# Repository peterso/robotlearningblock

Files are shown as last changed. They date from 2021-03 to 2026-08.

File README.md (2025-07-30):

# robotlearningblock

Welcome to the project repository for the Internet-connected task board, an electronic real-world benchmarking platform for evaluating robot manipulation skills. This project, known as the Digital Robotic Judge, or DR.J, contains the complete design of competition task boards used in the [Robothon Grand Challenge](https://www.robothon-grand-challenge.com) and the [euROBIN Manipulation Skill Versatility Challenge](http://sites.google.com/view/eurobin-msvc/home) to remotely assess manipulation performances over the Internet. Trial attempts are recorded by an on-board microcontroller which verifies the execution time and successful task completion through performance circuits. Task board telemetry is automatically published on a [web dashboard](https://cloud.kaaiot.com/wd-public/c1v9jqmgul2l1s47m6bg/dashboards/0d2f0e4c-6a80-4cf4-a48d-5b25fcb35ac0/50cdf30f-955e-4ccf-b13a-8e1d0281f68a?public_id=4e4990d1-dcab-4f1a-b1a6-8648e87bc5ad). The best automated robot solutions are collected, ranked, and verified with an expert jury over a video conference call. The top copmetition results are posted on a [leaderboard](http://github.com/peterso/robothon-grand-challenge) and developers are encouraged to share their project code in the form of competition submissions so that others can reproduce and improve on their results.

Industrial use cases collected through a survey are incorporated into the design of portable electronic task boards and made available to the community of robot developers to solve and put forth their best automated solution. New task board designs are developed annually. Share your use case to be considered in upcoming designs with the [Use Case Survey Google Form](https://forms.gle/XueGB4yPwioggSN97).

If you find this work helpful, please cite our [IEEE-RAM paper](https://ieeexplore.ieee.org/document/10378967). 

The concept of a crowdsourced robot solution for real-world use cases with the DR.J pipeline is shown below.

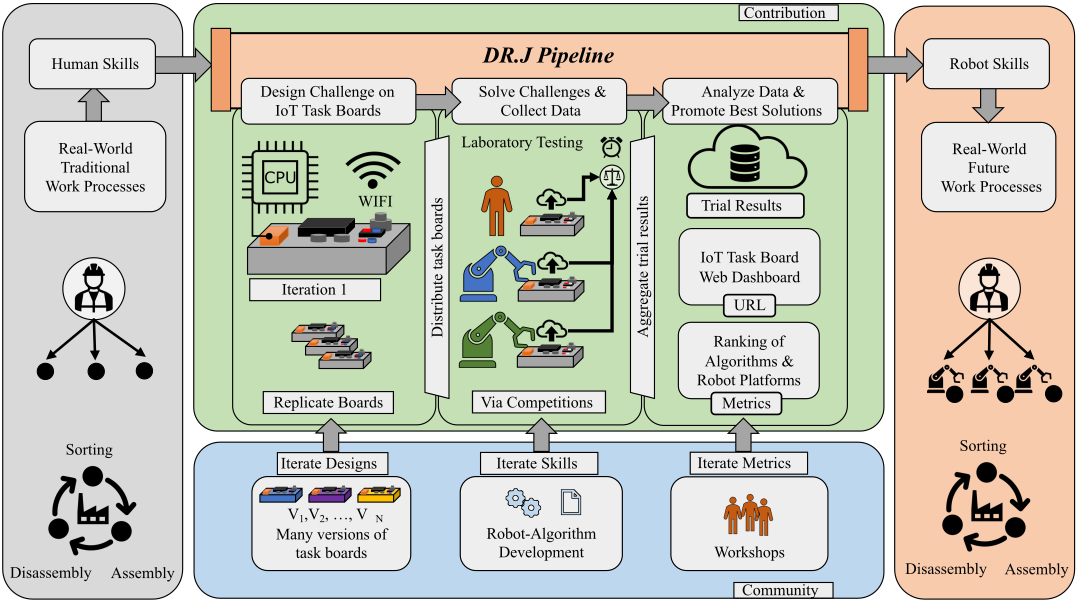
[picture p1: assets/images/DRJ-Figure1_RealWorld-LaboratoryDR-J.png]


## Quick Links

- IEEE-RAM Paper Digital Robot Judge: [DOI: 10.1109/MRA.2023.3336473](https://doi.org/10.1109/MRA.2023.3336473)
- 1-min Paper [Highlight Video](https://drive.google.com/file/d/1jVCkPBq7-JO2KUGaQfxDcgK1_qGyWVMT/view) 
- ERF 2022 Hackathon: Franka Emika Tactile Manipulation Benchmark Challenge: [Highlight Video](https://www.youtube.com/watch?app=desktop&v=eqpV09Kuc_o)
- Robothon Grand Challenge Competition [automatica website](https://automatica-munich.com/en/munich-i/robothon/)
- IROS 2024 Competiton: [euROBIN Manipulation Skill Versatility Challenge](http://sites.google.com/view/eurobin-msvc/home)
- Links to Web Dashboards for Deployed Task Boards:
  - [TBv2023: Teams Single Board View](https://cloud.kaaiot.com/wd-public/c1v9jqmgul2l1s47m6bg/dashboards/0d2f0e4c-6a80-4cf4-a48d-5b25fcb35ac0/50cdf30f-955e-4ccf-b13a-8e1d0281f68a?public_id=4e4990d1-dcab-4f1a-b1a6-8648e87bc5ad)
  - [TBv2023: Subtask Completion Times](https://cloud.kaaiot.com/wd-public/c1v9jqmgul2l1s47m6bg/dashboards/a8b5be5f-cc23-4724-8f06-3f67f8fef104?public_id=4e4990d1-dcab-4f1a-b1a6-8648e87bc5ad)
  - [TBv2021: Teams Single Board View](https://cloud.kaaiot.com/wd-public/c1v9jqmgul2l1s47m6bg/dashboards/dashboard2/931cb10a-3044-49c8-8530-5ce0951e291b?public_id=4e4990d1-dcab-4f1a-b1a6-8648e87bc5ad)
- Task Board Telmetry Emulator in Python (browser-based) [Replit](https://replit.com/@peterso/TaskBoardSimulator?v=1)
- Simulated Task Board Model on Mujoco for Offline Skill Development [Multiverse Github Project](https://github.com/Multiverse-Framework/Multiverse-Objects/tree/main/task_board)
- Request a physical task board [Task Board Request Google Form](https://forms.gle/EJiNF4A1qsrMpy8i6)
- Propose new tasks for future board designs [Use Case Survey Google Form](https://forms.gle/XueGB4yPwioggSN97)

## Project Description

The goal of the project is to provide an objective tool for measuring manipulation performance for both humans and robots. A microcontroller on the task box monitors the state of the mounted manipulation elements and reports state change events to a cloud-hosted dashboard to aggregate performance data. Device telemetry, including accelerometer data, is regularly logged to provide insight into the device's usage. Manipulation tasks are designed with objects that can be electronically verified to be in their designated start and goal positions. Trial protocols define sequences of actions on the task board and allow designers to create test scenarios. The execution time of subtasks within a protocol are recorded and automatically published on a web dashboard for consistent and convenient comparison with previous trial attempts. A modular framework for adding new task board objects was selected to encourage community members to design and build their own trial protocols.

An example demonstration of the internet-connected task board can be viewed on [YouTube](https://www.youtube.com/watch?v=1jdvIbDURSA). Here is the very first test run with a Franka Emika Panda robot in the lab [YouTube](https://youtu.be/LJFTypNZrFs).

A screenshot of a web dashboard from the 2021 Robothon Grand Challenge competition.

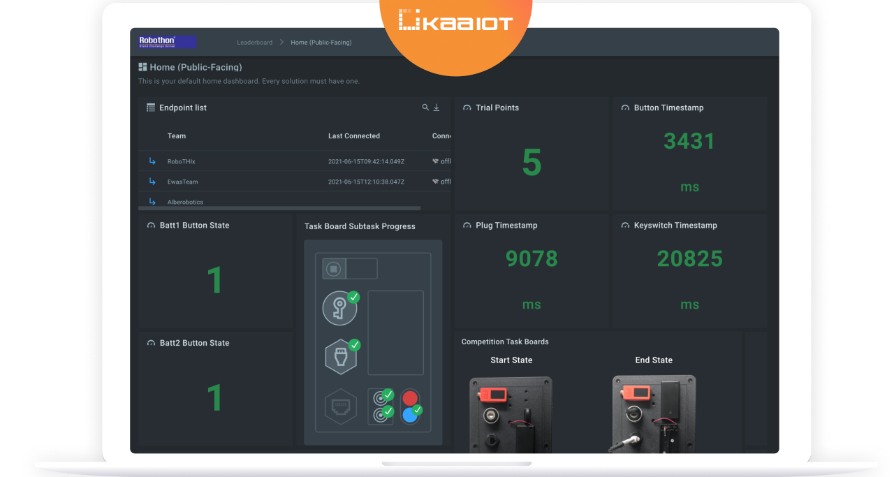
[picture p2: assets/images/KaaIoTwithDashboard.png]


Just for fun: The name is borrowed from the legendary basketball star [Julius "DR.J" Irving](https://www.youtube.com/watch?v=bWLXcg-V8FI). 

#### A little history on the smart task board development...
The internet-connected task board was first featured during the internationl robot manipulation competition, [Robothon Grand Challenge](https://www.robothon-grand-challenge.com) at automatica in 2021. The design of the task board has been expanded and reimplemented for the competition again in 2022 and has also been picked up by the pan-European robotics excellence collaboration project, [euROBIN](https://www.eurobin-project.eu/).

Here is an example setup of a exemplary robot testing setup with the task board.

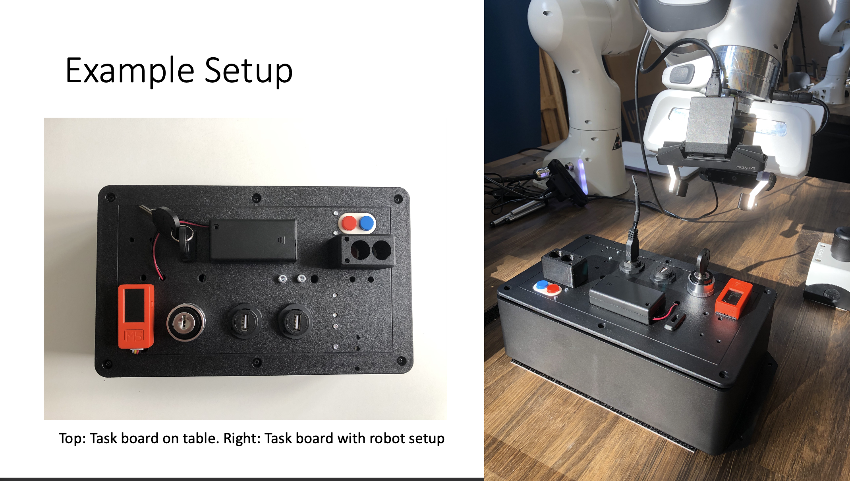
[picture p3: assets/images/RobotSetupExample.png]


The electronic task board allows for the direct comparison between a human and a robot performance to quantitatively measure the gap.

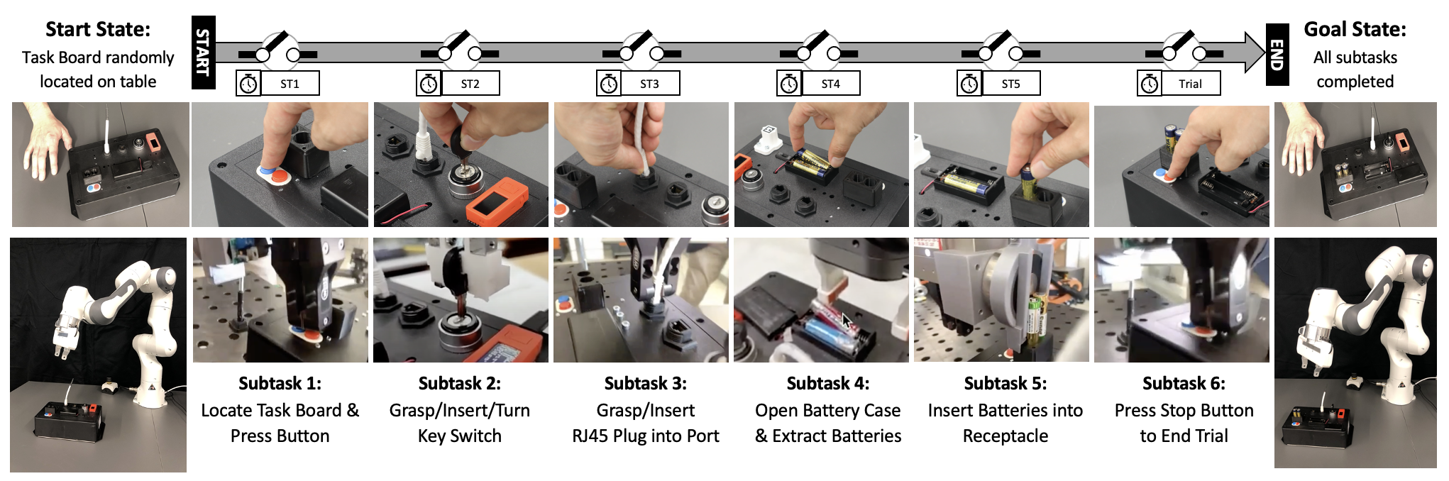
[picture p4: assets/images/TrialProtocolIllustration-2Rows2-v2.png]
TrialProtocolHumanRobot


Here is the trial protocol for the task board version TBv2021 used in the Robothon Grand Challenge in 2021 and 2022 to guide roboticists to develop reusable manipulation skills for e-waste sorting and disassembly.

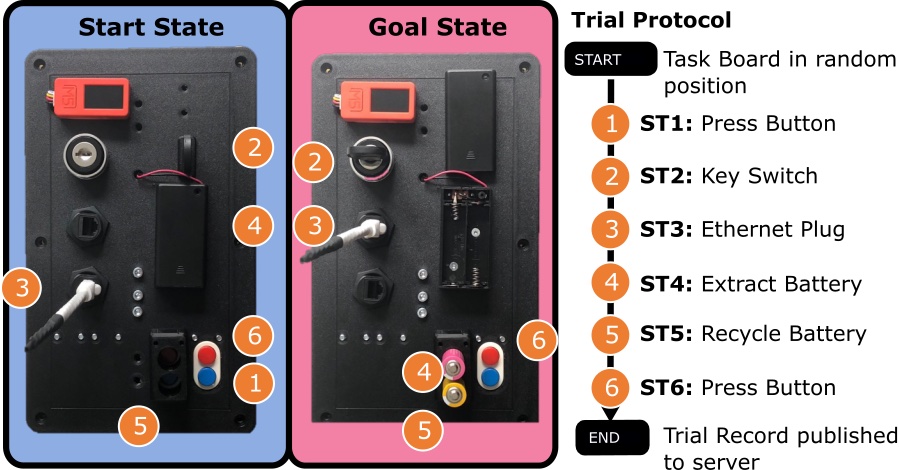
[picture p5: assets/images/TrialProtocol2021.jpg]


A new task board design (TBv2023) was designed and built to develop manipulation skills in performing electronic device assessments with a multimeter. The design was also adapted to meed the needs of the euROBIN network and was used in the Robothon Grand Challenge in 2023.

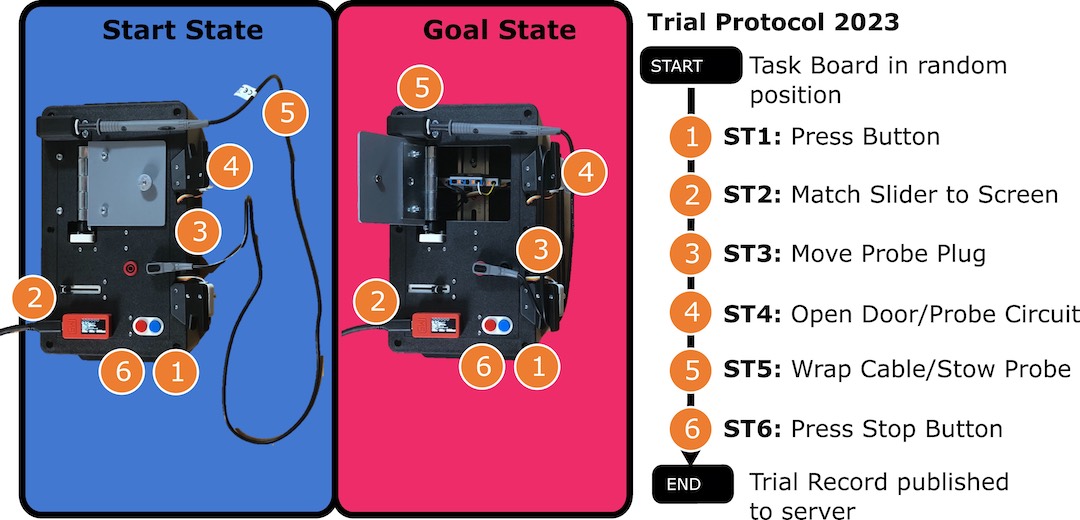
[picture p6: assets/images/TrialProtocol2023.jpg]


As part of the competition, teams were challenged to demonstrate the manipulation skills of their robot platform on an e-waste object of their choice in the "Bring-Your-Own-Device (BYOD) Challenge". Below are some examples of the successful demonstrations. 

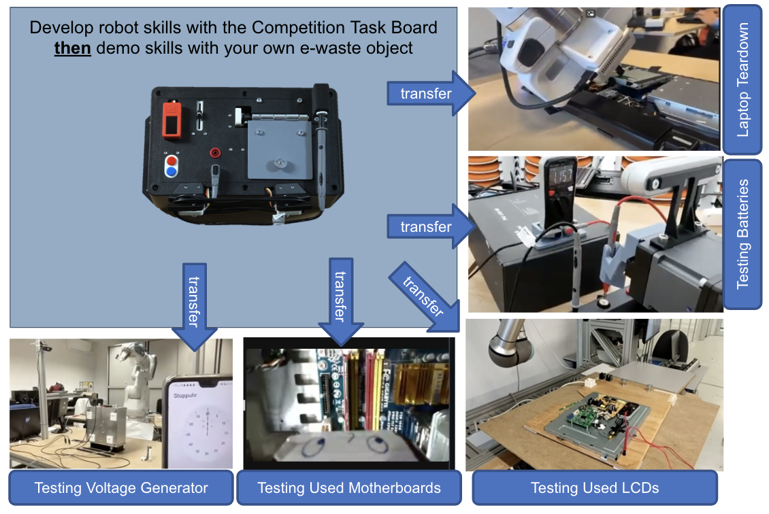
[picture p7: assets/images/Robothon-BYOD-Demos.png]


### Quick Start to connect a Task Board to the Web Dashboard

The microcontroller (orange component) has 3 Buttons and a USB-C charge/programming port:
- ***Power Button*** (side closest to USB-C), 
- ***Button A*** (next to screen, labeled M5), 
- ***Button B*** (side furthest from USB-C).

#### Turning on the Task Board ####

1. Toggle Power Manually = Hold Power Button for 2 seconds to turn on and 6 seconds to turn off.
2. Plugging in the uController will automatically turn on the device.

#### Connect board to the web dashboard over the internet with your preferred WiFi Network using your laptop or smartphone

1. Connect to Task Board SSID: “AutoConnectAP-task-board-###” where ### refers to the number on the sticker on the side of the box (Password: “robothon”)
2. A configuration screen should automatically open in a browser on your device. Otherwise, open web browser and go to URL: “192.168.4.1”.

3. Click the ”Configure” button to setup a new WiFi network connection. 

4. Select Desired WiFi from the scanned list.

5. Enter your SSID's WiFi password.

6. Click the “Save” Button. The new credentials will be saved to the microcontrollers EEPROM memory for future connections. The Task Board will attempt to connect to new WiFi. After it has successfully connected to the Internet over the new network the Home Screen will be displayed on the screen. 

#### Begin running experiments with the task board

1. Ensure the task board components are on their starting position prior to starting. The uController will display an alert on the screen if it detects an incorrect starting configuration.
2. Press Button A to start recording a trial run! Trial runs will be automatically recorded to the web dashboard. Scan the QR code on the sticker for more information.
3. Reset Trial Clock after a trialèPress Button B to reset the clock to zero.

#### Some Other Helpful Tips:

  • ***Offline/Local Mode:*** Use your task board without the internet by holding Button A down when powering on the device.

  • ***Abort an Active Trial:*** Stop an ongoing trial early by holding down the Red Push Button and pressing Button A.

### Detailed User Instructions 

The task board is designed to capture manipulation performance for use in the [Robothon Grand Challenge](https://www.robothon-grand-challenge.com). The microcontroller tracks users overall trial completion time, intermediate subtask completion times, earned trial points, and cumulative interaction force. Performance trials are initiated by the user after restoring the components to their start configuration and then pressing the M5 button. A countdown timer ends trial attempts after 10 minutes. When the task board is connected to the internet, the microcontroller publishes telemetry, during an active trial at 20Hz and 0.2Hz when idle, to a remote cloud server. An interactive web dashboard renders the trial data from the task board to provide transparent, remote observability into performance trials. Trials end when the countdown timer expires or when all sub-tasks are completed and the user presses the red stop button. Final trial results are displayed on the task board LED display and on the web dashbaord.

Trial protocols have a programmed time out of 10 minutes. While a trial is active, a red LED is illuminated on the controller. During active trials the agent under test should follow the trial protocol and complete all 5 subtasks on the task board as fast as possible. The results are recorded locally on the device and displayed on the controller's LED screen. 

Link to a [web simulator](https://replit.com/@peterso/TaskBoardSimulator?v=1) with Replit for testing new task board designs and trial protocols. NOTE: you will need to generate a new device token on the KaaIoT platform. 

Prior to running a new trial attempt, the trial protocol specifies the user must pick up and randomly place the task board in a new location in front of the user. An example of the location initialization is shown in the .gif below.

InitializeTaskBoard

After the task board location has been initialized, the user then presses the Trial Start button (M5 button) to begin a logged trial attempt. This .gif shows a human actor solving the 2021 trial protocol.

ManualTrialRun

#### Reading Task Board State over USB

When working with the task board, developers may want to read the task board state directly from the task board controller instead of referring to the web dashboard. To do this, use the python utility file to record the output to a local CSV file. See `/python/scripts/read-serial.py`.

### Core Design Features

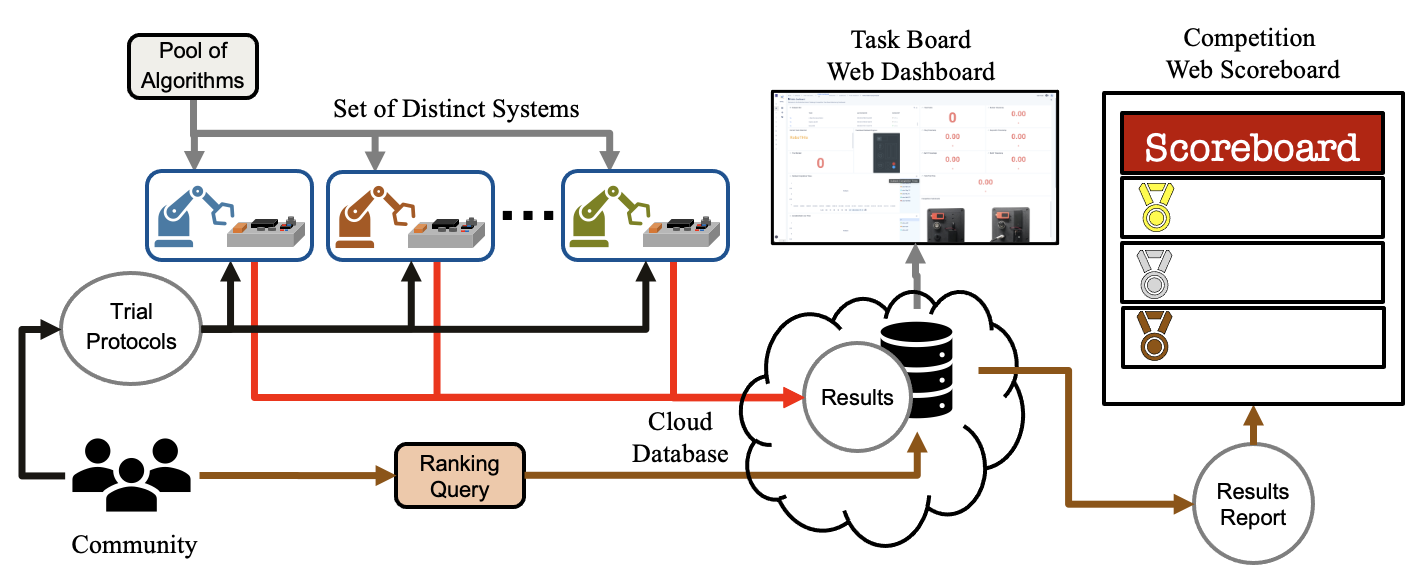
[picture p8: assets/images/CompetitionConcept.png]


The core design features of the task board microcontroller are:

**[Status] Feature Description**

- [x] task board monitors a digital state of all mounted manipulation elements
- [x] user can start a trial using the device without internet connection
- [x] task board reports the timestamps for each successful task interaction trial over USB
- [x] report the state of the task box over WiFi to the [Kaa internet dashboard](https://www.linkedin.com/safety/go?url=https%3A%2F%2Fcloud.kaaiot.com%2Fwd-public%2Fc1v9jqmgul2l1s47m6bg%2Fdashboards%2F0d2f0e4c-6a80-4cf4-a48d-5b25fcb35ac0%2F19addcfa-9cf1-42b3-8bd3-32a1feb4abdb%3Fpublic_id%3D4e4990d1-dcab-4f1a-b1a6-8648e87bc5ad&trk=flagship-messaging-web&messageThreadUrn=urn%3Ali%3AmessagingThread%3A2-YWRhYjQ3ZGYtZjc2YS00ZjZmLTkyZWEtMmMxNGNlNWE0ZjVjXzAxMw%3D%3D&lipi=urn%3Ali%3Apage%3Ad_flagship3_feed%3BBN9Td%2Bo8RjSi2fSXdyBvfQ%3D%3D) 
- [x] setup wifi greeter to allow user to supply own wifi ssid and password
- [x] report the state of the task box over USB
- [x] task board reports are integrated into a Microsoft Azure IoT dashboard
- [x] device has a digital twin that can be represented in a robot simulator i.e. Gazebo, Mujoco. 
- [ ] report the load cell readings on the task box surface
- [ ] integrate bluetooth power meter into task board telemetry
- [ ] enable internet connection network support for "Eduroam"

### NEW Feature Requests

- [x] Over-The-Air Updates to deploy new trial protocols to task boards in the field
- [x] Make the task board surface more stiff/rigid -> removed load cell and mount top plate to housing directly
- [ ] Add a automated testing procedure for a contract manufacturer to execute prior to shipping task boards
- [ ] Look into Device Management with BalenaOS for multiple OTA updates as an alternative to Kaa OTA
- [ ] Add ROS messages to the task board microcontroller to broadcast task results to robots

Please make a Github pull request with an updated README to add your new feature requests. Task board designs are updated annually and the firmware is continuously improved based on user feedback.

### Design Goals & System Architecture

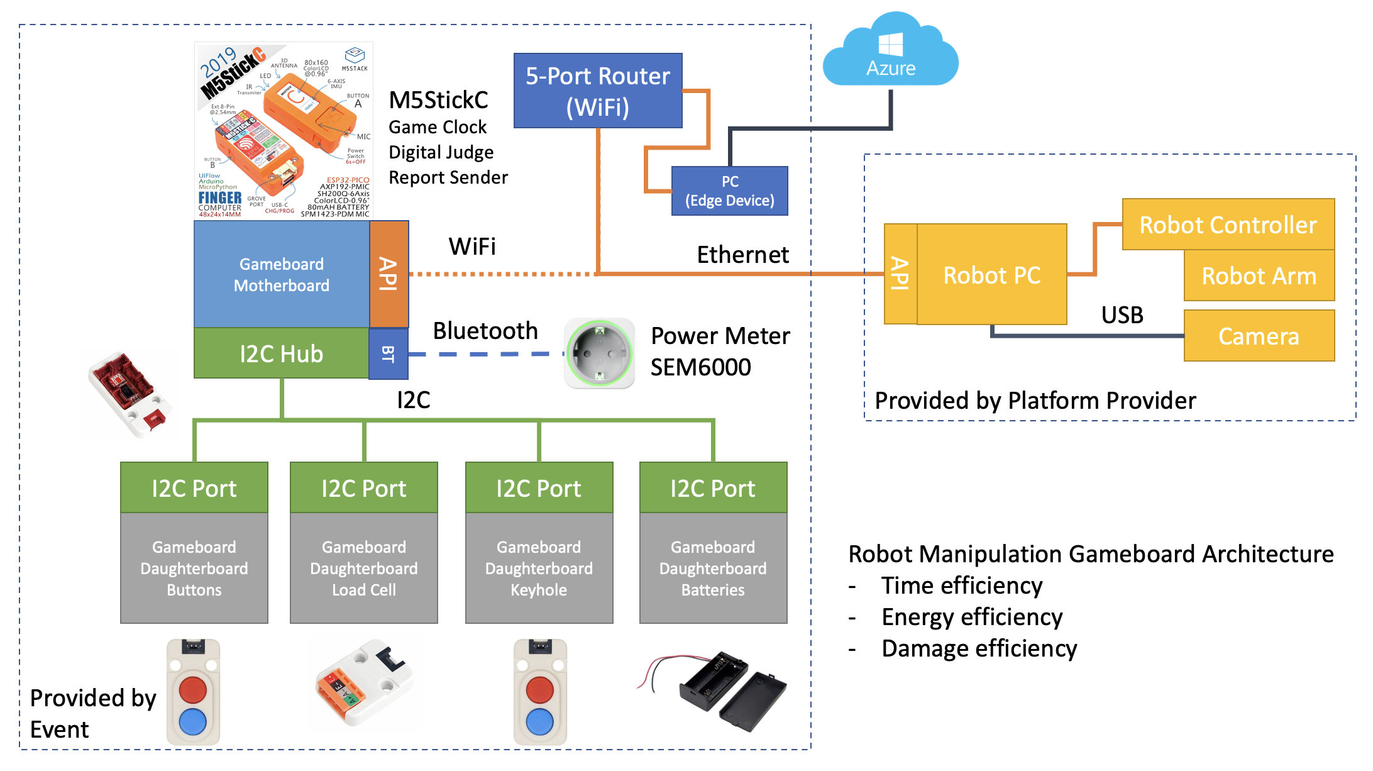
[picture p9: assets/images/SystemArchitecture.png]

Each task board is equipped with a microcontroller to remotely monitor its state and track usage statistics. Task boards are designed with the following features in mind:
- ***Affordable.*** Task board components should not exceed $200 to allow community members to build their own. The design is intended to be open sourced and remixed. 
- ***Portable.*** Task boards will have the capability to record trials untethered on battery power.
- ***Shippable.*** Task boards should be about the size of a laptop and weigh less than 1kg. For competition events, task boards can be shipped to participants to ensure everyone receives the same physical demonstrator setup.
- ***Traceability.*** Experiments performed on the task board can be automatically logged to a central web server for community members to share their development journey as well as easily download their experimental results.
- ***Extensible.*** Task board IO is extendable over an I2C bus to incorporate new task elements in future designs. 
- ***Networked.*** Each task board has the ability to report recorded trials to an online database.

### Relevant Design Documents

| Design Document       | TBv2021 | TBv2023 | TBv2025 |
|-----------------------|---------|---------|--------|
| Design BOM            | [TBv2021](https://docs.google.com/spreadsheets/d/1id1LLbRTHQwQDf9HCM8Hft5gwp9QI8y8CJt2JUEMMQk/edit?usp=sharing)        | [TBv2023](https://drive.google.com/file/d/1Rnd_u9MT5yowWGOLc9BP8yHH_inwEdMb/view?usp=sharing)        | Coming Soon |
| Assembly Drawing      | [PDF](https://drive.google.com/file/d/1hJSEHZe9U0Q7VRQKNKOsz96tIN9Y0mhF/view?usp=sharing)        | [PDF](https://drive.google.com/file/d/1tS-sQoqfd0bgX27vQssPpRKi-OBj2Tsp/view?usp=sharing)        |  Coming Soon |
| CAD Files             | [Onshape](https://cad.onshape.com/documents/9a15cff68aad2604a1373593/w/144a51d8ddacf96586ad0e0d/e/052e579b24ce3c66ae263023)        | [Onshape](https://cad.onshape.com/documents/db5a4ee49311d077447cc358/w/9c0b93db9a3945ee3cde6ada/e/5ab54cca5c27c6df318a9a63?renderMode=0&uiState=6720a79a1d02e666789b5f03)        |  [Onshape](https://cad.onshape.com/documents/aecd2bd76f7413bc4958e89c/w/35208a35a382e053eafac0d7/e/f99d3f5cc522bc6d6c1e4afb) |
| Assembly Instructions | [PDF](https://drive.google.com/file/d/1Znj0Do6tISIWl07lZ31Lp-qGyfQIPycp/view?usp=sharing)        | [PDF](https://drive.google.com/file/d/1LZS_wPafdJOO1Q0lu-8TDO9xGrxpoSBB/view?usp=sharing)        |  Coming Soon |
| Wiring Diagram | [PNG](/assets/images/TaskBoard-5Level-Wiring.png)        | [PDF](https://drive.google.com/file/d/1LZS_wPafdJOO1Q0lu-8TDO9xGrxpoSBB/view?usp=sharing)        |  Coming Soon |
| 3D Print Files        | ./assets        | ./assets        |  Coming Soon |
| CNC Files             | ./assets        | ./assets        |  Coming Soon |

### Task Board Deployment History
- ***2021*** An initial 15 task boards were fabricated for the Robothon 2021 competition at automatica.
- ***2022*** 20 task boards were built for the Robothon 2022 competition.
- ***2023*** A new design was released for Robothon 2023. 20 task boards were made for the competition.
- ***2024*** 15 more task boards (TBv2023) were made for the [euROBIN project](https://www.eurobin-project.eu/).
- ***2025*** A new design was released for Robothon 2025. 10 task boards were produced and distributed. 
- ***Order your own task board*** If you are interested in getting a pre-assembled task board to demonstrate your robot platform's capabilities or to follow along in the robot benchmark, please write an e-mail request with the model year [TBv2021/TBv2023/TBv2025] and the number of boards you wish to have along with your mailing address to peter@modularmotions.com.

### Circular Economy Articles inspiring Manipulation Task Selection
- WEF Report on battery recycling [Link to Article](https://www3.weforum.org/docs/WEF_A_New_Circular_Vision_for_Electronics.pdf)
- German Battery Collection with GRS Batterien [Link to Article](https://www.en.grs-batterien.de/grs-batterien/)
- Fun video from Curiousity Quest showing many e-waste handling processes [YouTube Video](https://www.youtube.com/watch?v=lMn-sDvgj4Q&ab_channel=curiosityquest)

### References
- [M5Stack Docs](https://docs.m5stack.com/)
- [M5Stack Community Forum](https://community.m5stack.com/category/17/m5-stick-stickc)
- [KaaIoT Arduino SDK](https://github.com/kaaproject/kaa-arduino-sdk)
- European Robotics Forum 2022 Franka Emika Tactile Manipulation Benchmark Challenge [Highlight Video](https://www.youtube.com/watch?app=desktop&v=eqpV09Kuc_o)
- 2022 Robothon Grand Challenge at [automatica/munich_i](https://www.robothon-grand-challenge.com), [Digital Kickoff Meeting Slides](https://drive.google.com/file/d/1OdqM9bOmNVIISuL4vuRz019WOS697p_8/view?usp=sharing), Award Ceremony [YouTube](https://www.youtube.com/watch?v=im-amiwJDgc&t=1s)
- 2023 Robothon Grand Challenge at [automatica/munich_i](https://www.robothon-grand-challenge.com), [Digital Kickoff Meeting Slides](https://drive.google.com/file/d/1x1t6U09iTEmM228orjCqwZNxu3CphAaz/view?usp=share_link), Award Ceremony [YouTube](https://www.youtube.com/watch?v=YmOT24pqiHU&t=559s)
- euROBIN Manipulation Skill Versatility Challenge at IROS 2024 [Competition Website](http://sites.google.com/view/eurobin-msvc/home)
- 2025 Robothon Grand Challege at [automatica/munich_i](https://automatica-munich.com/en/munich-i/robothon/)

### Citation 
If you find this work insightful to your research or you reference data from our competitions, please cite this work as ***Digital Robot Judge (DR.J): Building a Task-Centric Performance Database of Real-World Manipulation with Electronic Task Boards***. The manuscript is accepted for publication in IEEE Robotics and Automation Magazine as an open-access publication and an early release is available on [IEEE-Xplore](https://ieeexplore.ieee.org/document/10378967).

Bibtex:
```
@ARTICLE{So2024DRJ,
  author={So, Peter and Sarabakha, Andriy and Wu, Fan and Culha, Utku and Abu-Dakka, Fares J. and Haddadin, Sami},
  journal={IEEE Robotics & Automation Magazine}, 
  title={Digital Robot Judge: Building a Task-centric Performance Database of Real-World Manipulation With Electronic Task Boards}, 
  year={2023},
  volume={},
  number={},
  pages={2-14},
  doi={10.1109/MRA.2023.3336473}}
```

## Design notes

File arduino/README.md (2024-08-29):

# README Arduino Setup

The project is developed with the Arduino IDE.

If you want to flash the firware onto the M5StickPlus (ESP32) device then you will need to download the Arduino IDE and make the following changes to your configuration.

## Setup the Arduino IDE for the M5StickC

1. Add the M5Stack Library to your Library Path in Preferences [Github](https://docs.m5stack.com/en/quick_start/m5stickc_plus/arduino)
2. Install the "ESP32 Arduino" and "M5StickCPlus" Library using the Board Library Manager
3. Install the Wifi Manager Greeter "tzapu" using the Library Manager [Github](https://github.com/tzapu/WiFiManager#install-through-library-manager)

## How to flash new firmware onto your task board with Arduino IDE

1. Plug in the task board M5StickPlus unit to your PC with a USB cable.
2. Select the new device under the Port menu.
3. Select the board type as "M5StickC" under the Tools/Board menu.
4. Open the project folder containing the file you want to flash and compile and upload the .ino file. You should see an upload complete message in the command output section.
5. Verify the new firmware is working as expected by examining the serial output using the Serial Monitor tool.

## How to flash new firmware without the Arduino IDE
Use the flash-bin-no-ide.zip folder as a shareable object with the client. Compile the new target firmware with the Arduino IDE and then copy the *.bin files from your local PC into a new .zip folder.

The location of the *.bin files after compiling will be listed in the Arduino IDE in the terminal output when "verbose" flag for compiling is on in the Preferences menu. On a Mac, the location is something like: `/var/folders/bf/p280vkg91qj8wl5_1w4gn32h0000gn/T/arduino_build_168910/`

For Linux

Run the following two commands in a shell. Note, the second command parameters may need to be adapted depending on the file name during the binary export process and the port the task board controller is bound to.

`$ cd <PATH-to-UNZIPPED-FILES>`

`$ python esptool.py --chip esp32 --port /dev/ttyUSB0 --baud 1500000 --before default_reset --after hard_reset write_flash -z --flash_mode dio --flash_freq 80m --flash_size detect 0xe000 ./boot_app0.bin 0x1000 ./bootloader_dio_80m.bin 0x10000 ./stopwatch_m5stickcplus.ino.bin 0x8000 ./stopwatch_m5stickcplus.ino.partitions.bin`

Tip: On Linux, if you get a permission denied error on /dev/ttyUSB0 try the following command:
`sudo chmod a+rw /dev/ttyUSB0`

## Helpful Coding Resources
- M5Stack LCD Library Documentation: https://github.com/m5stack/m5-docs/blob/master/docs/en/api/lcd.md 
- ESP32 Persistent Memory Example: https://randomnerdtutorials.com/esp32-save-data-permanently-preferences/

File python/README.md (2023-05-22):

# README

### Setup PC to read the task board state over USB:
1. Install dependencies
`python -m pip install pyserial`

2. Grant access rights to the USB Port (Linux)
`sudo chmod 666 /dev/ttyUSB0`

3. Plug in the M5Stick Controller to the PC with a USB cable and verify the device is connected
`lsusb`

4. Open a new terminal window and run the python script `read-serial.py`

### Quick Start
A python script for reading input from a USB serial port and saving the streamed data to a file.

Run python script.
`python scripts/read-serial.py`

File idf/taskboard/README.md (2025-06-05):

# Robothon Task Board Firmware

A flexible and extensible firmware for Robothon Task Board.

Noteworthy features:

- Configurable task execution system with configurable patterns
- Modular sensor monitoring framework based on M5Stack
- REST API and Web Interface for remote control
- ROS 2 integration with custom message types
- Leaderboard logging and performance tracking

## Table of Contents

- [Robothon Task Board Firmware](#robothon-task-board-firmware)
  - [Table of Contents](#table-of-contents)
  - [Build firmware](#build-firmware)
  - [Data Model Overview](#data-model-overview)
    - [SensorMeasurement](#sensormeasurement)
    - [Sensor](#sensor)
    - [TaskStep](#taskstep)
    - [Task](#task)
  - [Controller Architecture Overview](#controller-architecture-overview)
    - [TaskBoardDriver](#taskboarddriver)
      - [Default Task](#default-task)
    - [ScreenController](#screencontroller)
    - [TaskExecutor](#taskexecutor)
    - [NonVolatileStorage](#nonvolatilestorage)
    - [HTTPServer](#httpserver)
    - [JSONHandler](#jsonhandler)
    - [WifiManager](#wifimanager)
    - [micro-ROS controllers](#micro-ros-controllers)
  - [Accessing the data model](#accessing-the-data-model)
    - [Example applications](#example-applications)
      - [REST API](#rest-api)
      - [Getting status from ROS 2](#getting-status-from-ros-2)
      - [Triggering a new Task from ROS 2](#triggering-a-new-task-from-ros-2)
      - [Triggering Task Board default task from ROS 2](#triggering-task-board-default-task-from-ros-2)
  - [Common actions](#common-actions)
    - [Connecting to a Wi-Fi network](#connecting-to-a-wi-fi-network)
    - [Connecting to a micro-ROS Agent](#connecting-to-a-micro-ros-agent)
      - [Using Docker](#using-docker)
      - [Building the micro-ROS Agent](#building-the-micro-ros-agent)
      - [Configuring the micro-ROS Agent](#configuring-the-micro-ros-agent)
    - [Recording a ROS 2 session](#recording-a-ros-2-session)
  - [Over-The-Air (OTA) updates](#over-the-air-ota-updates)
  - [Developing the Web Interface](#developing-the-web-interface)

## Build firmware

> [!IMPORTANT]
Make sure to configure the specific controller hardware and partition filename needed for your board as explained below in the menuconfig step.

The Robothon Task Board Firmware is built on top of the ESP-IDF framework.

The easiest way to get started is to use the ESP-IDF Docker image:

```bash
# Enter ESP-IDF Docker image
docker run -it --rm -v /dev:/dev --privileged espressif/idf:release-v5.3

# Install dependencies inside the Docker container
pip3 install catkin_pkg lark-parser colcon-common-extensions empy==3.3.4

# Clone the repository
git clone https://github.com/peterso/robotlearningblock

# Initialize the submodules
cd robotlearningblock
git submodule update --init --recursive

# Change to the project directory
cd /robotlearningblock/idf/taskboard

# Configure the project
idf.py menuconfig
# M5STACK controller -> M5STACK hardware (Select the hardware of the M5 HW on your board)
# Partition Table -> Custom partition CSV file
#     "partitions.csv" (default) for M5STACK StickC Plus2 and M5STACK CORE2
#     "partitions_stickcplus.csv" for M5STACK StickC Plus (version with 4MB of FLASH memory)

# Deploy to the board and monitor execution
idf.py build flash monitor
```

To update a `M5STACK StickC Plus` (the version with 4MB of FLASH memory), it is necessary to use a different baud rate for flashing:

```bash
# Deploy to the board and monitor execution
idf.py build && idf.py -b 500000 flash && idf.py monitor
```

To run `idf.py` from any additional terminal attached to the Docker, the following command is needed:

```bash
source /opt/esp/idf/export.sh
```

## Build ROS 2 messages

In case that the ROS 2 messages are modified, they need to be built from a ROS 2 environment.

This is only necessary when the compiler shows an error similar to this:

```bash
/robotlearningblock/idf/taskboard/main/microros/MicroROSTypes.hpp:217:27: error: 'robothon_taskboard_msgs__msg__TaskStatus' {aka 'struct robothon_taskboard_msgs__msg__TaskStatus'} has no member named 'score'
```

To build the ROS 2 messages run `colcon build` in the `extra_ros_packages` directory.

```bash
# Navigate to the messages directory
cd extra_ros_packages

# Build the messages
colcon build

# Source the ROS 2 workspace
source install/local_setup.bash
```

If the above commands are not available in your current environment, it is possible to start a ROS 2 Jazzy Docker container to read and modify the files in the host filesystem via a shared volume.

```bash
# Go to the taskboard directory in your host filesystem
cd robotlearningblock/idf/taskboard

# Run the Jazzy Docker container with a volume pointing to the current directory
docker run -it --rm --privileged --net=host -v $(pwd):/robotlearningblock/idf/taskboard ros:jazzy

# Navigate to the messages directory
cd /robotlearningblock/idf/taskboard/extra_ros_packages

# Build the messages
colcon build

# Source the ROS 2 workspace
source install/local_setup.bash
```

After building the messages, go back to the espressif environment, clean the project and build it again:

```bash
# Clean and build the project
idf.py clean
idf.py build
```

If you used the ROS 2 Jazzy Docker approach, to point to the already existing project in your host filesystem, you can also use the Docker volume option with the ESP-IDF container:

```bash
# Go to the repository root
cd robotlearningblock

# Run the ESP-IDF Docker container with a volume pointing to the current directory
docker run -it --rm -v /dev:/dev -v $(pwd):/robotlearningblock --privileged espressif/idf:release-v5.3

# Navigate to the taskboard directory inside the Docker container
cd /robotlearningblock/idf/taskboard

# Clean and build the project
idf.py clean
idf.py build
```

## Data Model Overview

The Robothon Task Board Firmware is built around a hierarchical data model where **Tasks** is the main component.

A **Task** is a named group of **TaskSteps** that must be completed in an specific order.

A **TaskStep** is a single condition that must be met during task execution.
It is composed of a **Sensor** and a **SensorMeasurement**.

It is fulfilled when the **Sensor** reading matches the expected value defined in the **SensorMeasurement**.

A **Sensor** represents a physical or aggregated input device that can be read, updated, and monitored.

An example of a physcal **Sensor** can be a button attached to a GPIO.
On the other hand an aggregated **Sensor** can be a virtual sensor that combines multiple physical sensors, for example the activation of two buttons at the same time.

A **SensorMeasurement** represents a single reading from a sensor.

This element holds a value and a type.
Types can be boolean values, analog values or even complex values like a 3D vector.

```mermaid
classDiagram
    class Task
    class TaskStep
    class Sensor
    class SensorMeasurement

    Task "1" *-- "1..*" TaskStep : contains
    TaskStep *-- Sensor : monitors
    TaskStep *-- SensorMeasurement : expects
    Sensor --> SensorMeasurement : produces
```

### SensorMeasurement

**SensorMeasurement** are represented globally in `SensorMeasurement` class found in `sensor/SensorMeasurement.hpp`.

Current implementation has support for:

| Type      | Description   | C++ Type                     |
| --------- | ------------- | ---------------------------- |
| `BOOLEAN` | Boolean value | `bool`                       |
| `ANALOG`  | Analog value  | `float`                      |
| `VECTOR3` | 3D vector     | `SensorMeasurement::Vector3` |

### Sensor

**Sensor** are represented globally in `Sensor` class found in `sensor/Sensor.hpp`.

Beyond that, there is also provided a `AnalogFilteredSensor` class in`sensor/AnalogFilteredSensor.hpp` that extends `Sensor` and adds a averaging filter to the analog readings.

### TaskStep

**TaskStep** are represented globally in `TaskStep` class found in `task/TaskStep.hpp`.

Currently, there are three types of `TaskStep`:

- `TaskStepEqual`: Exact value matching with configurable tolerance.
- `TaskStepGreaterEqualThan`: Threshold monitoring for analog values.
- `TaskStepEqualToRandom`: Exact value matching for random target.

**TaskSteps** can be extended by creating new classes that inherit from `TaskStep`.

### Task

**Task** are represented globally in `Task` class found in `task/Task.hpp`.

Three types of `Task` are provided:

- `SequentialTask`: Steps must be completed in order.
- `ParallelTask`: Steps can be completed in any order.
- `SimultaneousConditionTask`: All conditions must be satisfied simultaneously.

**Tasks** can be extended by creating new classes that inherit from `Task`.

## Controller Architecture Overview

The Robothon Task Board Firmware implements a set of modular controllers that manage different aspects of the system and interacts with the data model.

### TaskBoardDriver

A **TaskBoardDriver** is an interface that describes certain configuration of a Task Board.
It is resposible for creating and updating a set of **Sensor** objects.

Currently a single implementation is provided in `TaskBoardDriver_v1` class found in `hal/board/TaskBoardDriver_v1.hpp`.

#### Default Task

The **TaskBoardDriver** implementation is in charge of providing a default **Task** that will be executed.
This default taks is the one that can be started just by pressing the button on the Task Board.

This default task may require some preconditions to be met before it can be executed, that is a certain well known Task Board state.

### ScreenController

The **ScreenController** is an object that handles the display output of the Task Board.

### TaskExecutor

The **TaskExecutor** is an object that handles that execution of a **Task**.

This component will be responsible for monitoring the status of a **Task** and update other elements of the system (such as the **ScreenController**) accordingly.

### NonVolatileStorage

THe **NonVolatileStorage** is an object that handles the persistance of data.

### HTTPServer

The **HTTPServer** is an interface that handles HTTP requests.

This element will serve the REST API and Web Interface.

Check section [Developing the Web Interface](./web_interfaces/README.md) for more information.

### JSONHandler

The **JSONHandler** is a helper class that converts the Data Model to and from JSON.

### WifiManager

The **WifiManager** is an object that handles the network connectivity of the Task Board.

### micro-ROS controllers

The Robothon Task Board Firmware provides a ROS 2 integration that allows the system to communicate with other ROS 2 nodes by means of micro-ROS.

In order to implement the ROS 2 integration the following classes are provided:

- `MicroROSTypes`: Conversions between micro-ROS and Robothon Task Board data types.
- `MicroROSController`: Handles micro-ROS Client status, micro-ROS Agent connection, and creation and destruction of micro-ROS entities.
- `MicroROSTask`: An specialization of `Task` that allows to create a `Task` from a ROS 2 action.
- `MicroROSTaskExecutor`: Coordinates the interaction between the `TaskExecutor` and the `MicroROSController` by means of handling the `MicroROSTask` lifecycle.

Beyond that classes, a comprehensive translation of the Task Board data model to ROS 2 messages is provided in `extra_ros_packages/robothon_taskboard_msgs` package.

## Accessing the data model

The Robothon Task Board Firmware exposes two primary interfaces for accessing the data model:

- **REST API**: Provides a set of endpoints for interacting with the system via HTTP requests.
- **ROS 2 Integration**: Allows the system to communicate with other ROS 2 nodes.

This two interfaces exposes access and control over the system and the data model in the following way:

| Action                            | REST API            | ROS 2                                                                      |
| --------------------------------- | ------------------- | -------------------------------------------------------------------------- |
| Task Board Status                 | `/taskboard_status` | `/robothon_taskboard_status [robothon_taskboard_msgs/msg/TaskBoardStatus]` |
| Current Task Status               | `/task_status`      | `/robothon_task_status [robothon_task_msgs/msg/TaskStatus]`                |
| Execute a new Task <sup>1</sup>   | Not available       | `/taskboard_execute_task [robothon_taskboard_msgs/action/ExecuteTask]`     |
| Leaderboard                       | `/leaderboard`      | Not available                                                              |
| System Status                     | `/system_status`    | Not available                                                              |
| Configure micro-ROS Agent address | `/microros`         | Not available                                                              |

<sup>1</sup> An empty call to this interface will trigger the default task.

### Example applications

#### REST API

An example of a webpage that consumes the REST API can be found in `web_interfaces` folder.

This webpage is also served by the **HTTPServer** controller in the endpoint `/`.

#### Getting status from ROS 2

For subscribing to the Task Board status, you can use the following command:

```bash
ros2 topic echo /robothon_taskboard_status
```

or

```bash
ros2 topic echo /robothon_task_status
```

#### Triggering a new Task from ROS 2

An example of a ROS 2 application that sends a new Task to the Task Board can be found in `extra_ros_packages/robothon_taskboard_goal_sender` folder.

This example application can be built as a normal ROS 2 package and run as a node:

```bash
# Build the ROS 2 package
cd extra_ros_packages
colcon build

# Source the ROS 2 workspace
source install/local_setup.bash

# Run the ROS 2 node
ros2 run robothon_taskboard_goal_sender goal_sender
```

#### Triggering Task Board default task from ROS 2

An ROS 2 application that triggers the Task Board default task can be found in `extra_ros_packages/robothon_taskboard_default_task_sender` folder.

This example application can be built as a normal ROS 2 package and run as a node:

```bash
# Build the ROS 2 package
cd extra_ros_packages
colcon build

# Source the ROS 2 workspace
source install/local_setup.bash

# Run the ROS 2 node
ros2 run robothon_taskboard_default_task_sender goal_sender
```

## Common actions

Robothon Task Board Firmware assummes that every **TaskBoardDriver** implementation will have the following buttons registered as sensors:

- `BUTTON_A`: M5Stack button A
- `BUTTON_B`: M5Stack button B
- `BUTTON_PWR`: M5Stack power button
- `RED_BUTTON`: On board red button
- `BLUE_BUTTON`: On board blue button

By means of these buttons, the following basic configuration actions can be performed:

| Action                            | Trigger                                                           |
| --------------------------------- | ----------------------------------------------------------------- |
| Reset WiFi and start provisioning | Press `RED_BUTTON` and `BLUE_BUTTON` at the same time during boot |
| Start in local mode (No Wifi)     | Press `BUTTON_A` during boot                                      |
| Start default task                | Press `BUTTON_B`                                                  |
| Start default task (human mode)   | Press `BUTTON_B` and `BUTTON_PWR` at the same time                |
| Cancel current task               | Press `BUTTON_A`                                                  |

### Connecting to a Wi-Fi network

After the Task Board is started in provisioning mode, it will create a Wi-Fi network.

The board will notify in its screen the SSID of the new network and the IP address of the board.

The Wi-Fi SSID is "Robothon Task Board " + the last three characters of the MAC address of the device.

By reaching the IP address of the board in a web browser, the Web Interface will be shown:

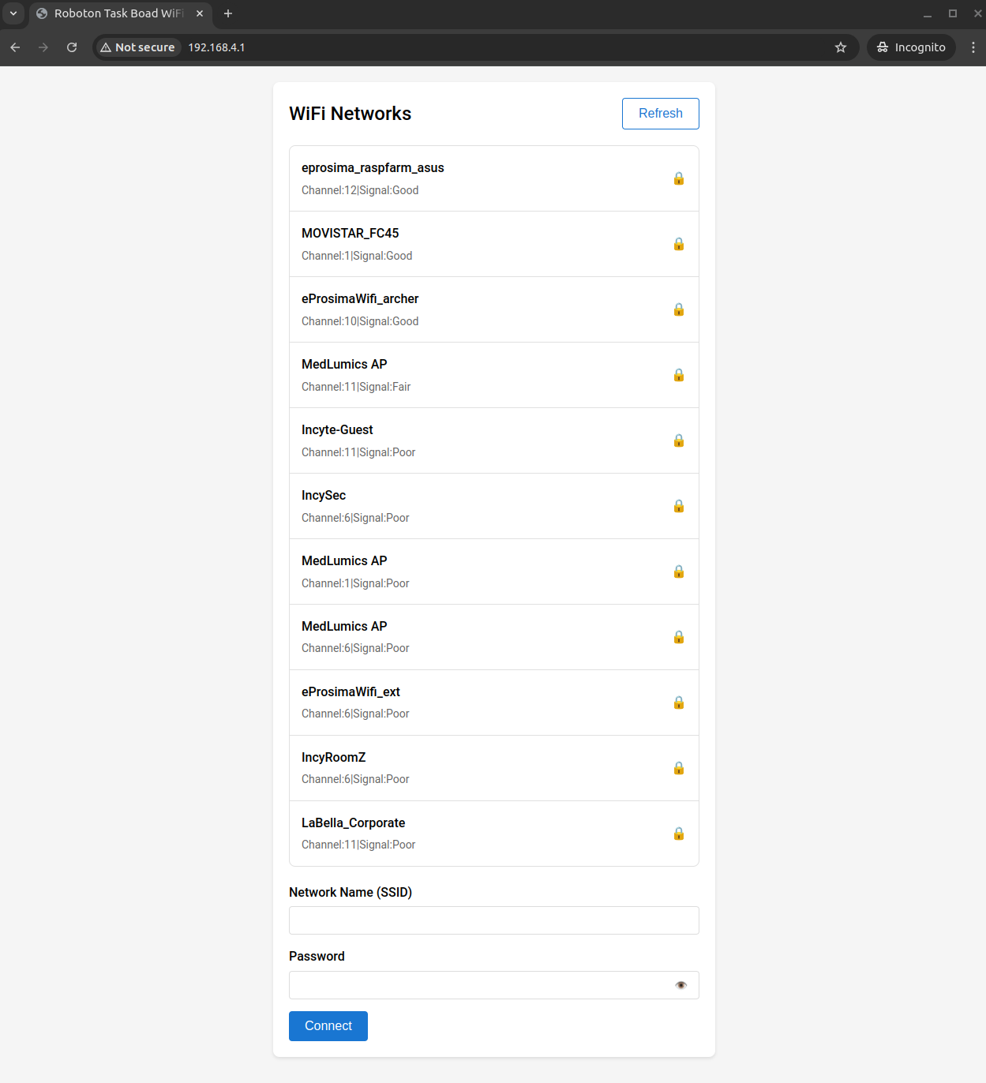
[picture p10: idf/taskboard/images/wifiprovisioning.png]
WiFi Provisioning Robothon Task Board WiFi Provisioning


### Connecting to a micro-ROS Agent

> [!IMPORTANT]
Ensure that the micro-ROS Agent version matches the ROS 2 distribution.

#### Using Docker

In order to **connect to a micro-ROS Agent** to start the ROS 2 integration, an micro-ROS Agent can be instantiated using docker:

```bash
docker run -it --rm --privileged --net=host --ipc host microros/micro-ros-agent:$ROS_DISTRO udp4 --port 8888 -v4
```

#### Building the micro-ROS Agent

Also, the micro-ROS Agent can be built locally:

```bash
# Install dependencies
apt update
apt install ros-$ROS_DISTRO-micro-ros-msgs

# Create a workspace
mkdir -p microros_agent_ws/src
cd microros_agent_ws

# Clone the micro-ROS Agent
git clone -b $ROS_DISTRO https://github.com/micro-ROS/micro-ROS-Agent.git src/micro-ROS-Agent

# Build the micro-ROS Agent
source /opt/ros/$ROS_DISTRO/setup.bash
colcon build
```

After building the micro-ROS Agent, it can be started using:

```bash
cd microros_agent_ws

source /opt/ros/$ROS_DISTRO/setup.bash
source install/local_setup.bash

ros2 run micro_ros_agent micro_ros_agent udp4 --port 8888 -v5
```

#### Configuring the micro-ROS Agent

The IP address and port of the micro-ROS Agent can be configured using the Web Interface or the REST API.

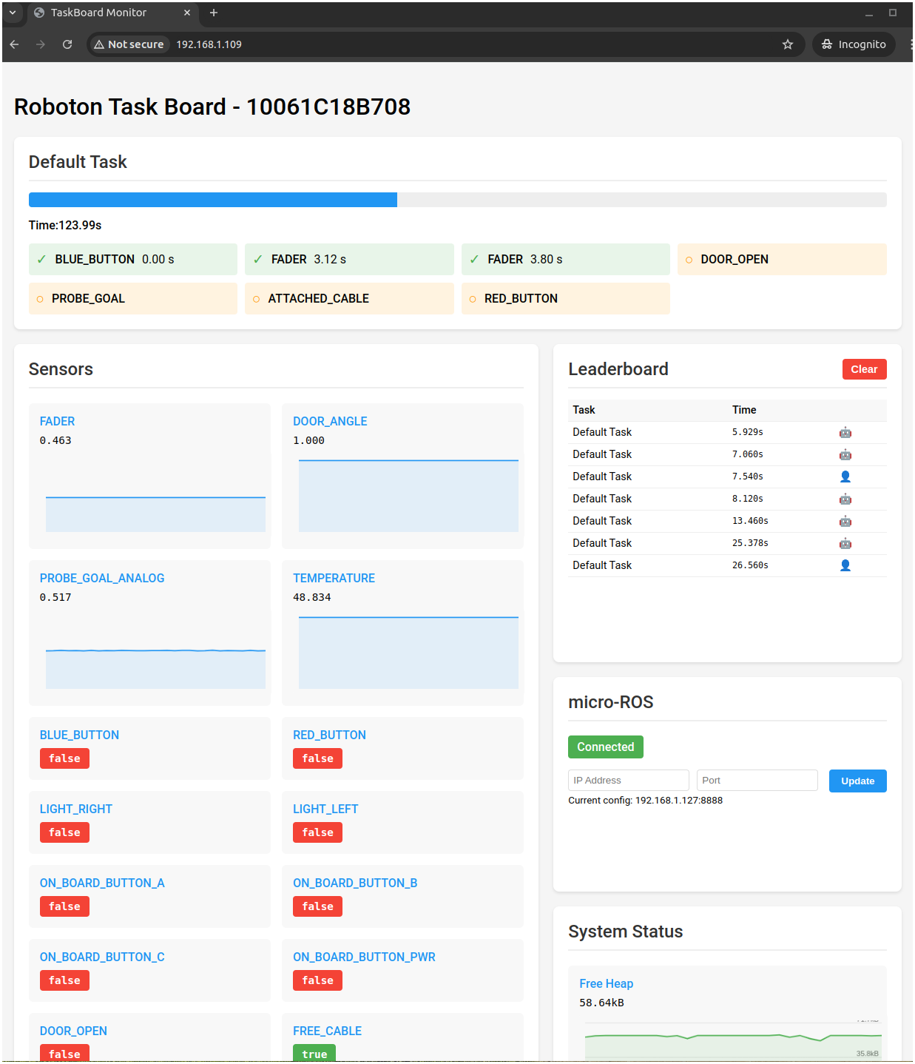
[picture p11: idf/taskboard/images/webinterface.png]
Web Interface Robothon Task Board Web Interface


### Recording a ROS 2 session

To record a ROS 2 session the usage of [Vulcanexus Recorder & Replay](https://docs.vulcanexus.org/en/jazzy/rst/introduction/tools/recordreplay.html).

To use the recorder, the easiest way is using docker:

```bash
cd robotlearningblock/idf/taskboard
docker run -it --rm --privileged --net host --ipc host  -v $(pwd)/extra_ros_packages/record_replay_session:/shared_folder eprosima/vulcanexus:jazzy-desktop ddsrecorder -c /shared_folder/config.yml
```

To allow the DDS Recorder to append custom ROS 2 types into `.mcap` file (to use them in platforms such as Foxglove Studio), ensure that the following command is run at least once during the recording session:

```bash
cd robotlearningblock/idf/taskboard
docker run -it --rm --privileged --net host --ipc host  -v $(pwd)/extra_ros_packages:/shared_folder eprosima/vulcanexus:jazzy-desktop bash /shared_folder/record_replay_session/match_topic_types.sh
```

Former command will generate a .mcap file in the `extra_ros_packages/record_replay_session` folder.

In order to replay the session, the following command can be used:

```bash
docker run -it --rm --privileged --net host --ipc host  -v $(pwd)/extra_ros_packages/record_replay_session:/shared_folder eprosima/vulcanexus:jazzy-desktop ddsreplayer -i /shared_folder/[session_name]
```

**Remember to add extra topics to `extra_ros_packages/record_replay_session/config.yml` if they need to be recorded**

## Over-The-Air (OTA) updates

The Robothon Task Board Firmware supports Over-The-Air (OTA) updates.

The OTA update procedure relies on Github Releases and the ESP-IDF OTA mechanism.

The followinf steps are done to perform an OTA update:

1. The Task Board is connected to a Wi-Fi network.
2. The newest release information is retrieved using HTTPS for a [well-defined end-point](./main/network/OTAUpdater.hpp#L25)
3. The latest release name (in format `vX.Y.Z`) is compared to the [current firmware version](./main/version.hpp).
4. If a newer version is available, the firmware will ask the user to confirm the update using the Task Board buttons and screen.
5. If the user confirms the update, the firmware will download the first asset whose name starts with `taskboard.bin` from the release.
6. After the firmware upgrade is done, the Task Board will reboot and start the new firmware.

## Developing the Web Interface

The Web Interface is served by the **HTTPServer** controller in the endpoint `/`.

The Web Interface is built using Vanilla JavaScript, HTML 5 and CSS 3, in order to keep it simple, lightweight and embeddable in flash memory.

HTML files are stored in the `web_interfaces` folder.
Those files are minified and embedded into a C header file using [`generate_embedded_html.py`](./web_interfaces/generate_embedded_html.py) script.

In order to update the Web Interface, the following steps can be followed:

1. Modify the HTML files in the `web_interfaces` folder.
2. You can use a local web server to test the changes

```bash
cd web_interfaces
python3 -m http.server

# Go to localhost:8000 in your web browser and ensure that "Device IP" (in the bottom left corner) is pointing to the Task Board IP address.
```

3. Run the `generate_embedded_html.py` script to generate the embedded HTML file.

```bash
# Inside web_interfaces folder
cd web_interfaces

# Install dependencies
pip3 install -r requirements.txt
apt install xxd

# Generate embedded files
python3 generate_embedded_html.py
```

4. Copy the generated `.h` files to the firmware folder: [`main/network/webpages/`](./main/network/webpages/).
5. Rebuild and flash the firmware.

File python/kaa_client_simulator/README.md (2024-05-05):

# README Task Board Python Simulator

The task board has a python simulator that emulates MQTT packets sent from a physical task board. This is useful for debugging. Currently, there is a simulator environment configured with Replit.com.

View and run the simulator: [Task Board Simulator](https://replit.com/@peterso/TaskBoardSimulator#main.py)

A goal would be to create simulator that runs locally. However the Replit sim seems to be working fine and is currently working for free.

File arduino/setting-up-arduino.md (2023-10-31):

# A Beginner's Guide to setting up the Arduino IDE with the M5StickC Development Board

This guide explains how to setup the Arduino IDE on a development PC in order to program a new task board microcontroller from M5Stack.

## Instructions for setting up on Linux Ubuntu
1. Download the zip file of the arduino ide from the arduino website
https://www.arduino.cc/en/guide/linux
2. Unzip the file
3. Open the arduino IDE by running the arduino.sh file in a terminal
4. Add the Espressif URL to the Board Manager list in Preferences (Arduino IDE/Preferences/Settings/Additional boards manager URLs):
    https://dl.espressif.com/dl/package_esp32_index.json
5. Add the board files for ESP32 using the Board Manager
6. Add the libraries for ESP32 and M5StickC
7. Install pyserial with pip3. (Optional)

## Verify your Setup
Plug in the M5StickC board and see if it is recognized by the computer. It should be viewable in the arduino IDE under Mene/Tools/Port as /dev/cu.usbserial.###### on MacOS or /dev/ttyUSB# on Linux.

Before uploading to the board, confirm the following settings for the board target, port, and baud rate in the IDE under the Menu/Tools:
- Board = M5StickC, 
- Port = /dev/ttyUSB0, (or similar) 
- Baud = 1500000

Note that each task board controller should have a unique Token in order to be recognized by Kaa. Tokens have the general form of `task_board_###` where ### refers to the number on the sticker applied to the side of the task board. The token is specified in the firmware in the `secrets.h` file as variable `SECRET_TOKEN`.

If you are creating a new task board device you will need to generate a new device and token on the KaaIoT platform. You will need sufficient permissions from the KaaIoT account (member of the 'Dev Team') to generate new tokens. To generate a new token go to the [Kaa Device Management Portal](https://cloud.kaaiot.com/devices/device-management/), select the correct Application, this project is currently using "smart task board proto" with App Version Name="c1v9jqmgul2l1s47m6bg-v0" and generate a new token by clickgin on "Add device" in the top right of the window. 

The current subscription with Kaa is limited to ~~15~~, ~~50~~, 100 devices. 

## Flashing new firmware to the task board microcontroller
After verifying all the steps above you can flash the new firmware to the microcontroller with the "upload" command.

Wait for the upload to take place (~1min). When the upload is finished, you should see the message upload complete in the IDE and the screen on the M5StickC unit should restart.

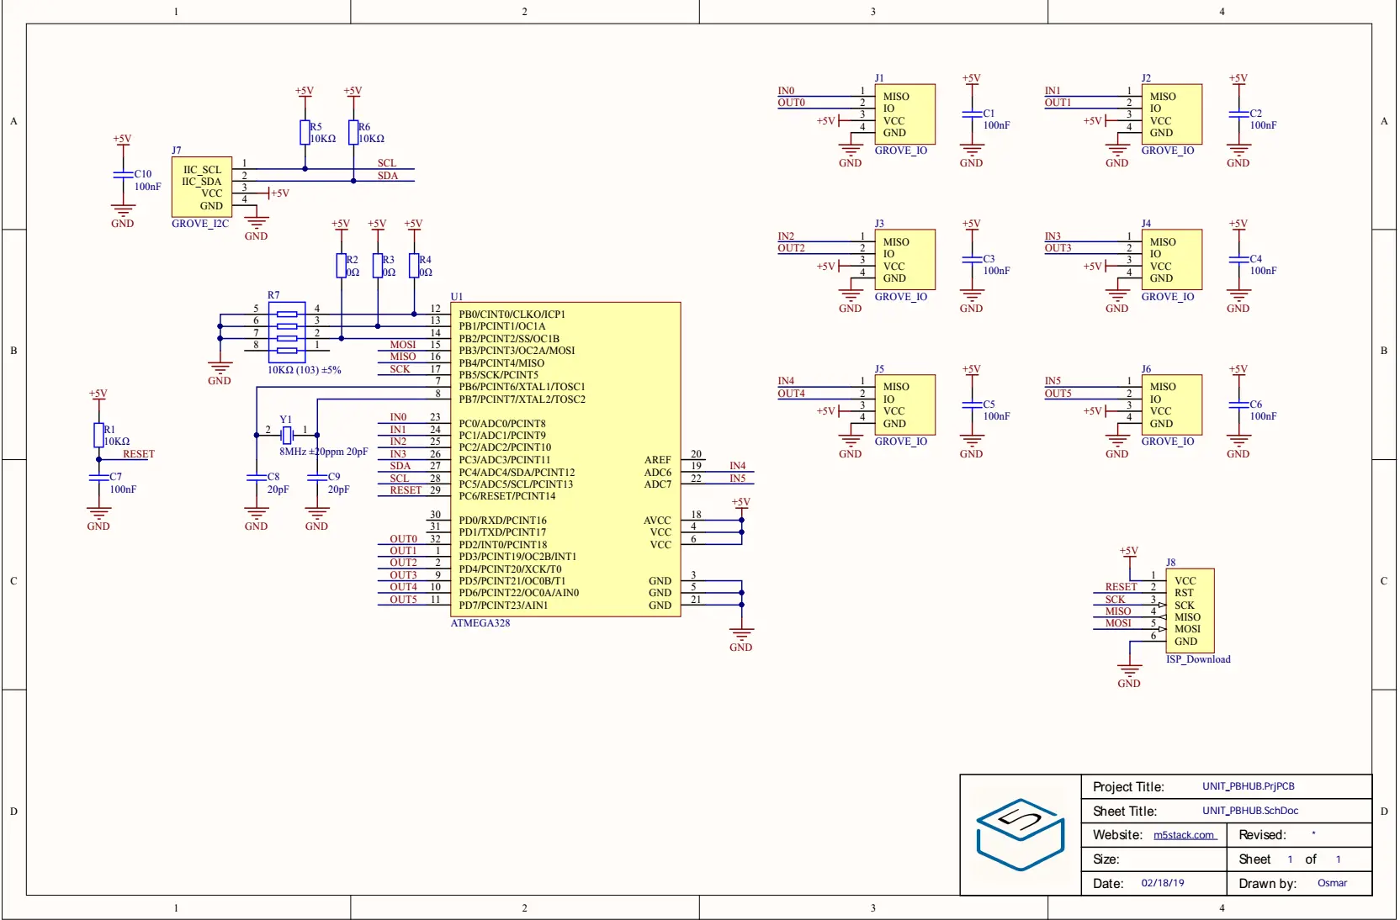
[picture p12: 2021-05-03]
datasheets/pbhub_schematic.png

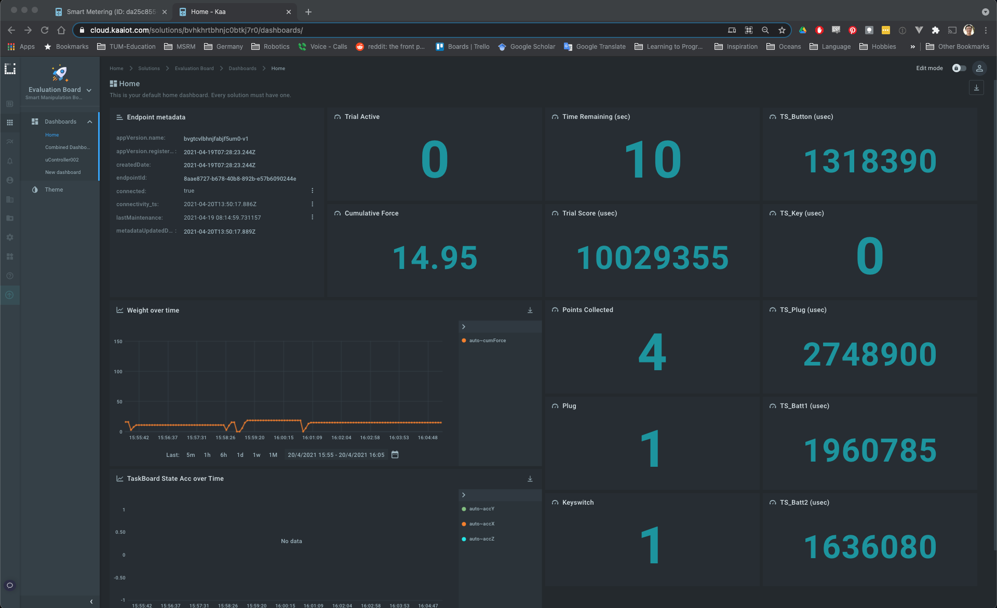
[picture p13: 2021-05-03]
assets/images/Kaa-Dashboard-SingleBoard.png

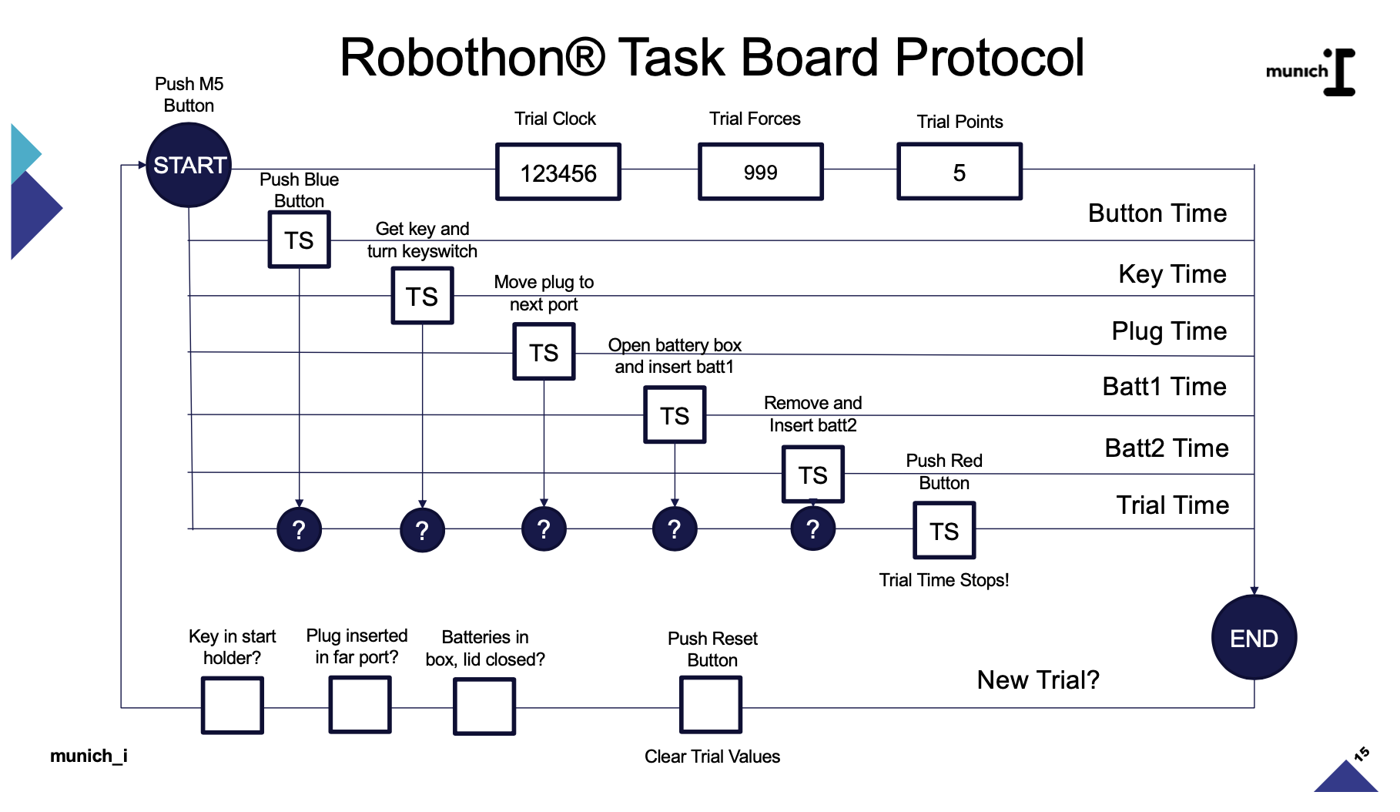
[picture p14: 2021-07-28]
assets/images/TaskBoardProtocolMap.png

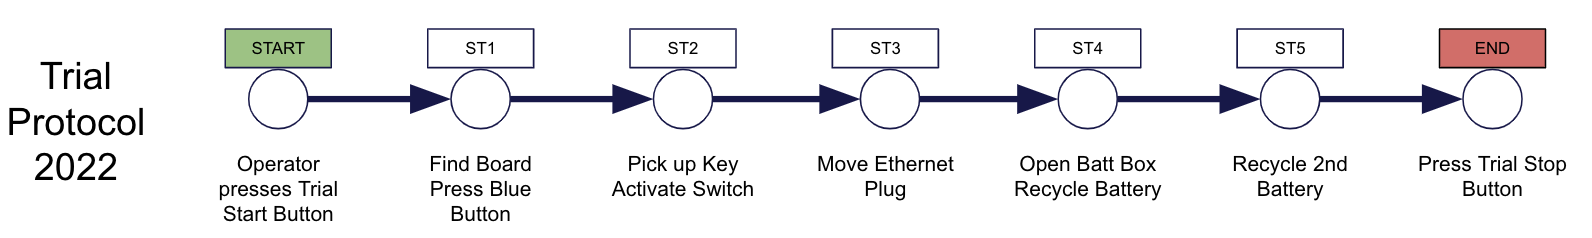
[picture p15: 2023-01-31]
assets/images/TrialProtocol2022.png

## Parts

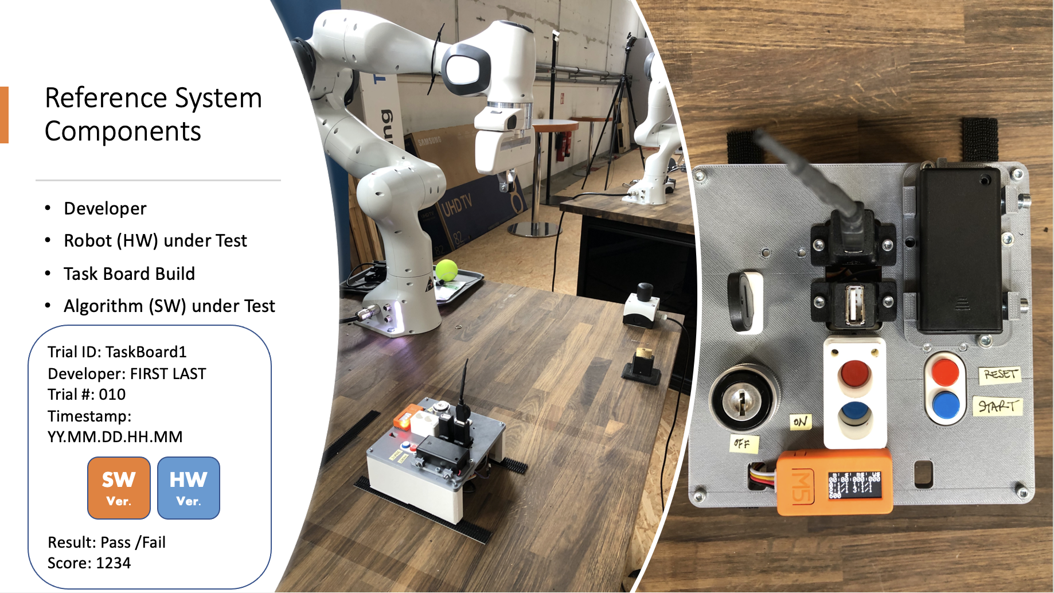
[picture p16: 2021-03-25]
assets/images/ReferenceSystemComponents.png

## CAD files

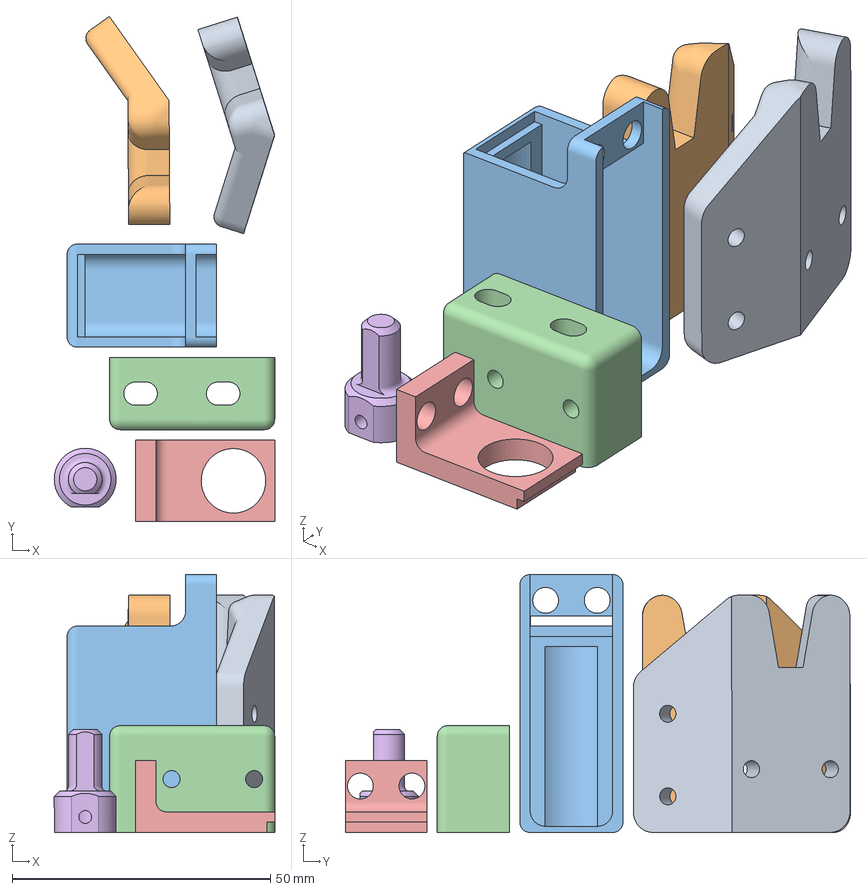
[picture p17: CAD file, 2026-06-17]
assets/manufacturing/TBv2023/TBv2023_PrintCompleteSet.3mf
42.7 x 97.9 x 50.0 mm
Cable_Winding - Cable Wrap Post Left.stl
Cable_Winding - Cable Wrap Post Right.stl
2-Part 90deg Plug Holder - Snap Cover.stl
Angle Sensor Mounting Bracket - Angle Sensor Mounting Bracket.stl
2-Part 90deg Plug Holder - L-bracket.stl
Angle Sensor-Hinge Adapter.stl

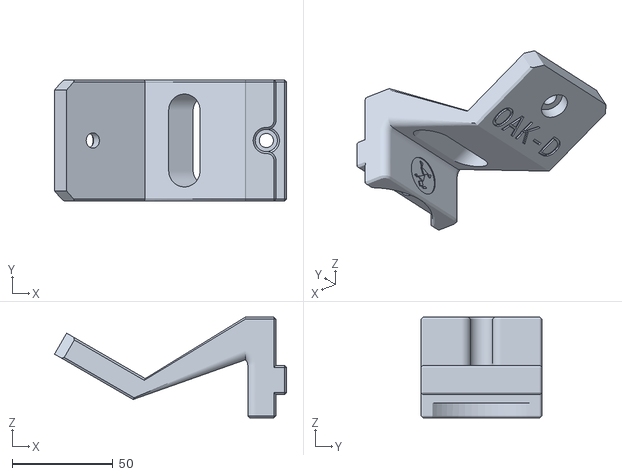
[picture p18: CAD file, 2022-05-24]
assets/manufacturing/Panda_OAK-D - Panda_OAK-D_Camera_Mount.stl
115.0 x 60.0 x 50.0

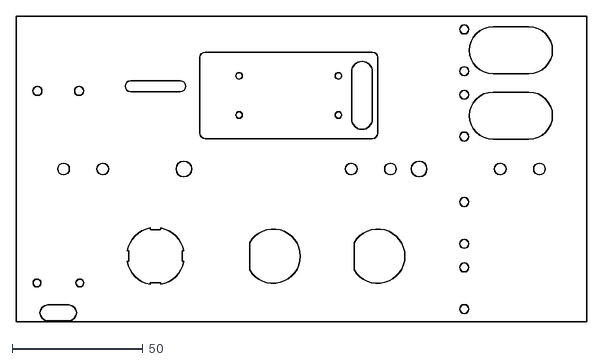
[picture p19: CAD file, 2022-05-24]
assets/manufacturing/TBv2021-TBv2022/CNC/CU-3286-MB - Box Lid TBv2022.dxf
218.3 x 116.7

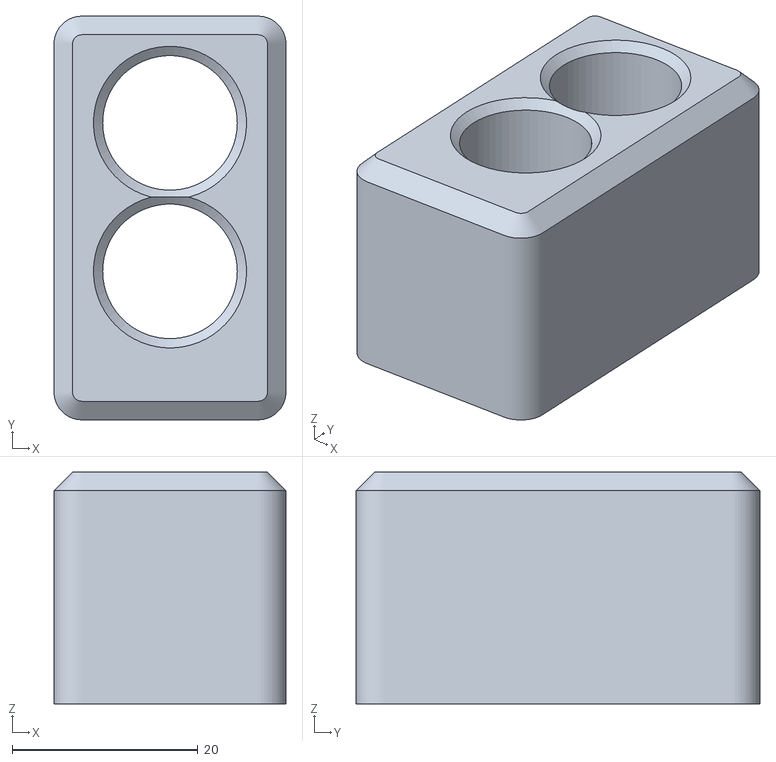
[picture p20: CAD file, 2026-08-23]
assets/manufacturing/TBv2021-TBv2022/STLs/eTBv2021_ButtonCoverPlate3.stl
25.0 x 43.5 x 25.0

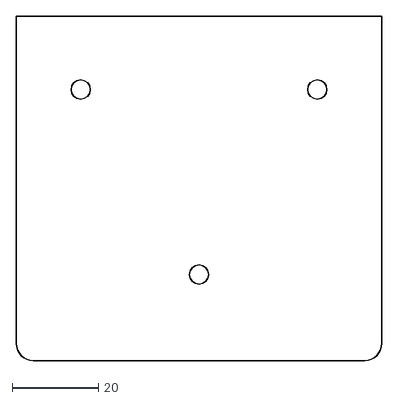
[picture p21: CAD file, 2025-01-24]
assets/manufacturing/TBv2023/CNC/Door - MillingExport.dxf
85.0 x 80.0

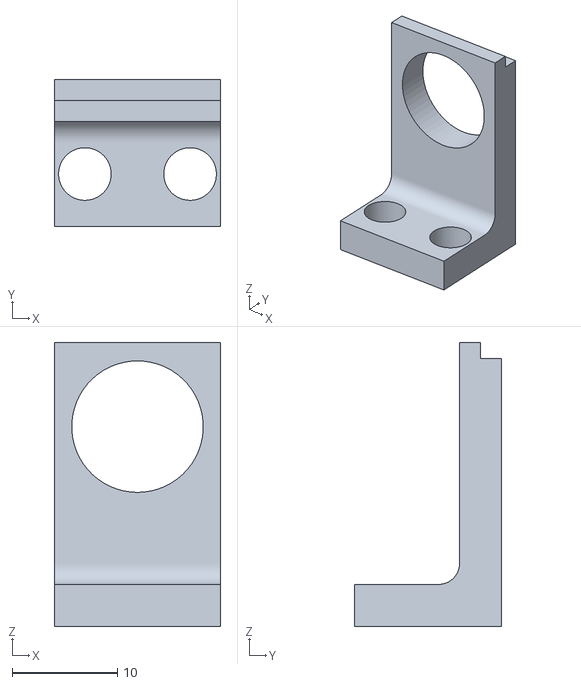
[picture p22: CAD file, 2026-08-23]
assets/manufacturing/TBv2023/STLs/2-Part90degPlugHolder-L-bracket.stl
15.8 x 14.0 x 27.0

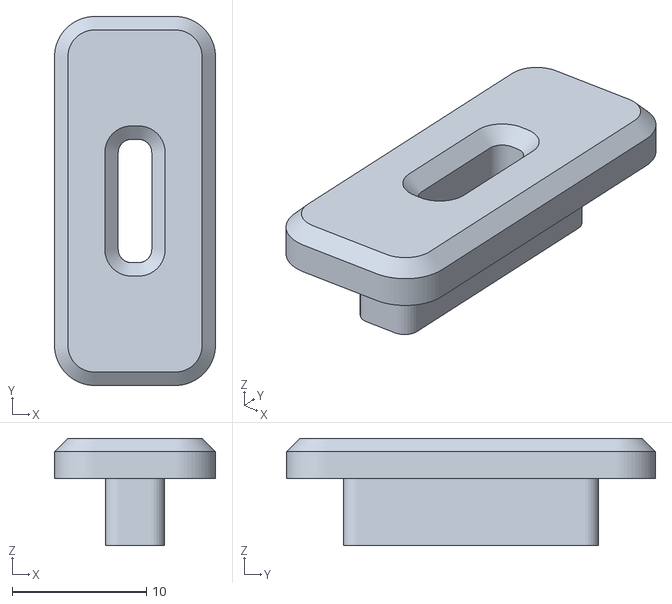
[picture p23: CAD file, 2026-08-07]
assets/manufacturing/TBv2021-TBv2022/STLs/eTBv2021_KeyHolderInsert.stl
12.0 x 27.5 x 8.00

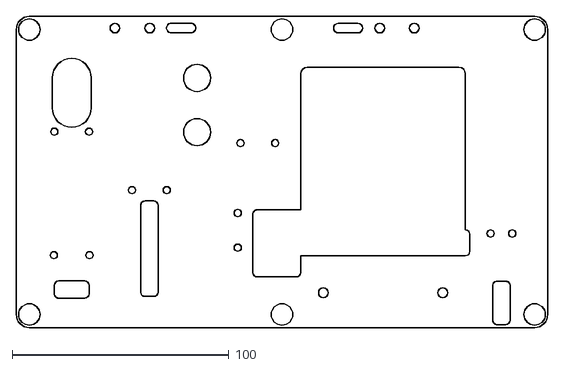
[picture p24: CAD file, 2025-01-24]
assets/manufacturing/TBv2023/CNC/CU-3286-MB - Box Lid V3-updated.dxf
245.0 x 143.4

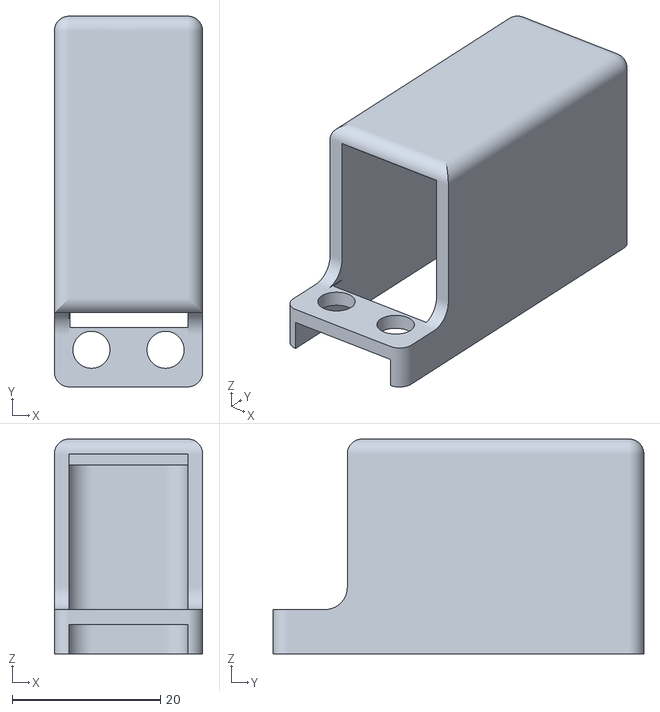
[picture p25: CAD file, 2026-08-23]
assets/manufacturing/TBv2023/STLs/2-Part90degPlugHolder-SnapCover.stl
20.0 x 50.0 x 29.0

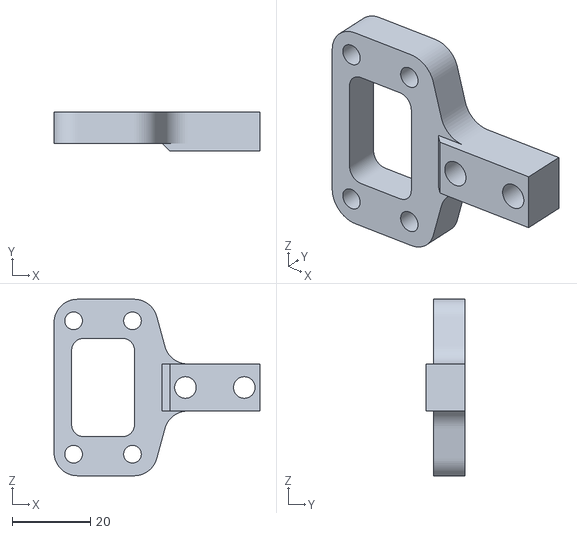
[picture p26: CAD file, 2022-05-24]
assets/manufacturing/TBv2021-TBv2022/STLs/CU-3286-MB parts - Load Cell Mount 8mm.stl
52.5 x 10.0 x 45.0

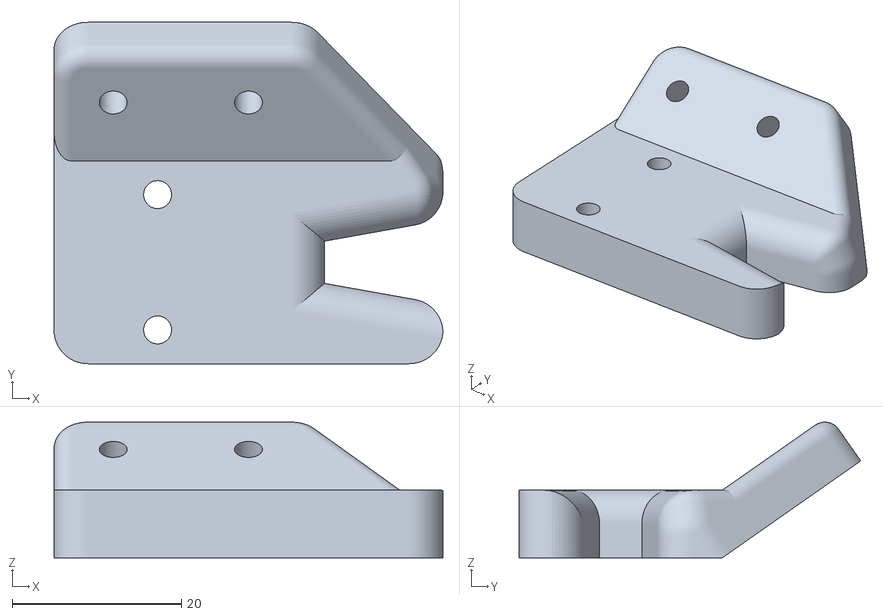
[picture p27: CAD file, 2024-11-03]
assets/manufacturing/TBv2023/STLs/Cable_Winding - Cable Wrap Post Right.stl
46.0 x 40.4 x 16.1

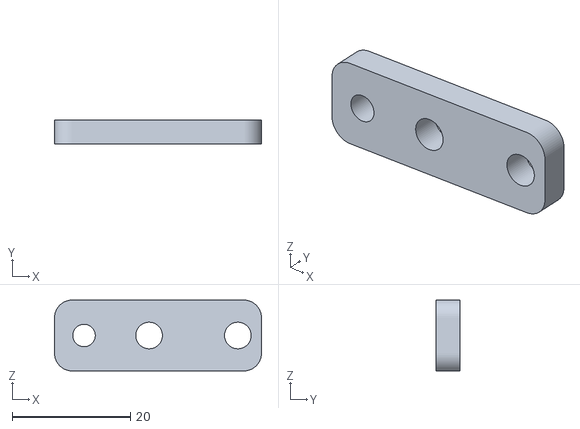
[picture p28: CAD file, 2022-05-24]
assets/manufacturing/TBv2021-TBv2022/STLs/CU-3286-MB parts - LC Standoff.stl
35.0 x 4.00 x 12.0

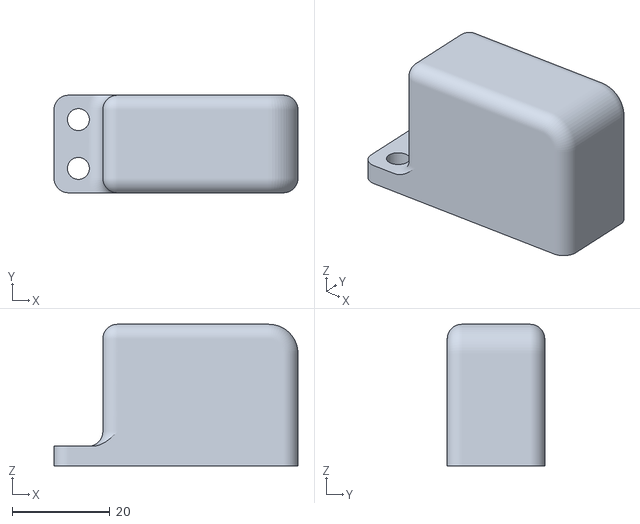
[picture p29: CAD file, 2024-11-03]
assets/manufacturing/TBv2023/STLs/Probe Holder - Probe Holder.stl
50.0 x 20.0 x 29.0

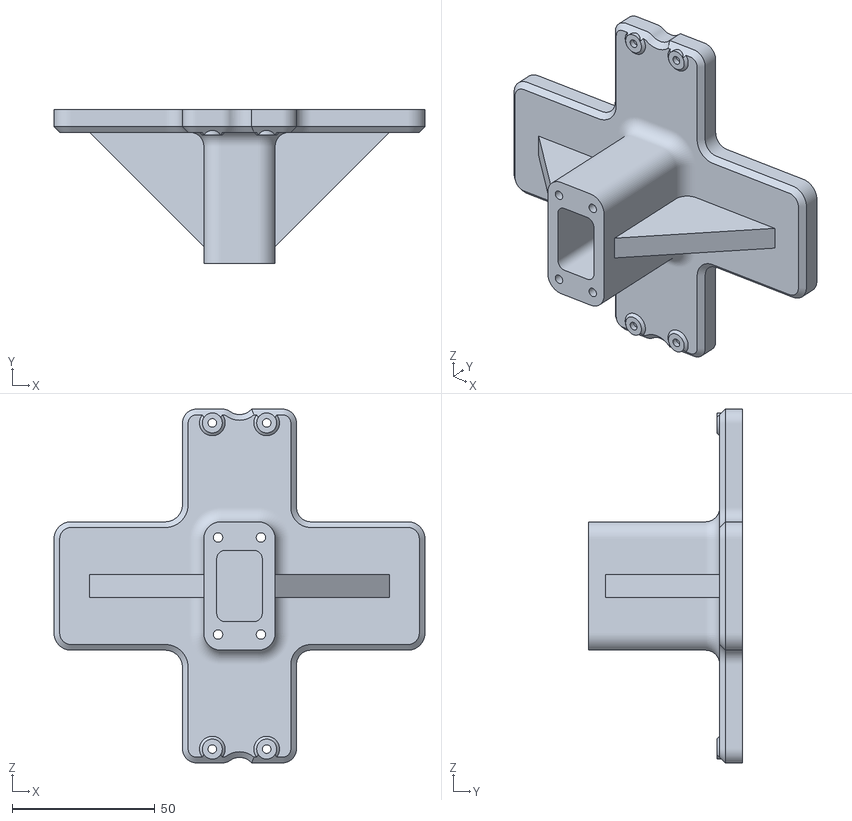
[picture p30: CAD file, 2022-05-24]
assets/manufacturing/TBv2021-TBv2022/STLs/CU-3286-MB parts - Load Cell Stand v2.stl
130.0 x 54.0 x 124.0

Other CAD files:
assets/manufacturing/TBv2023/TBv2023_PrintCompleteSet.gcode.3mf
assets/manufacturing/TBv2023/STLs/Angle Sensor-Hinge Adapter.stl
assets/manufacturing/TBv2021-TBv2022/STLs/CU-3286-MB parts - uControllerSpacer.stl
assets/manufacturing/TBv2023/STLs/Angle Sensor Mounting Bracket - Angle Sensor Mounting Bracket.stl
assets/manufacturing/TBv2021-TBv2022/STLs/CU-3286-MB parts - 3286-CT.stl
assets/manufacturing/TBv2023/STLs/Cable_Winding - Cable Wrap Post Left.stl

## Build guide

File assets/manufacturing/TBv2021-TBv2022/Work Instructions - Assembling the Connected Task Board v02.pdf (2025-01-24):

# Assembly of the Connected Smart Box

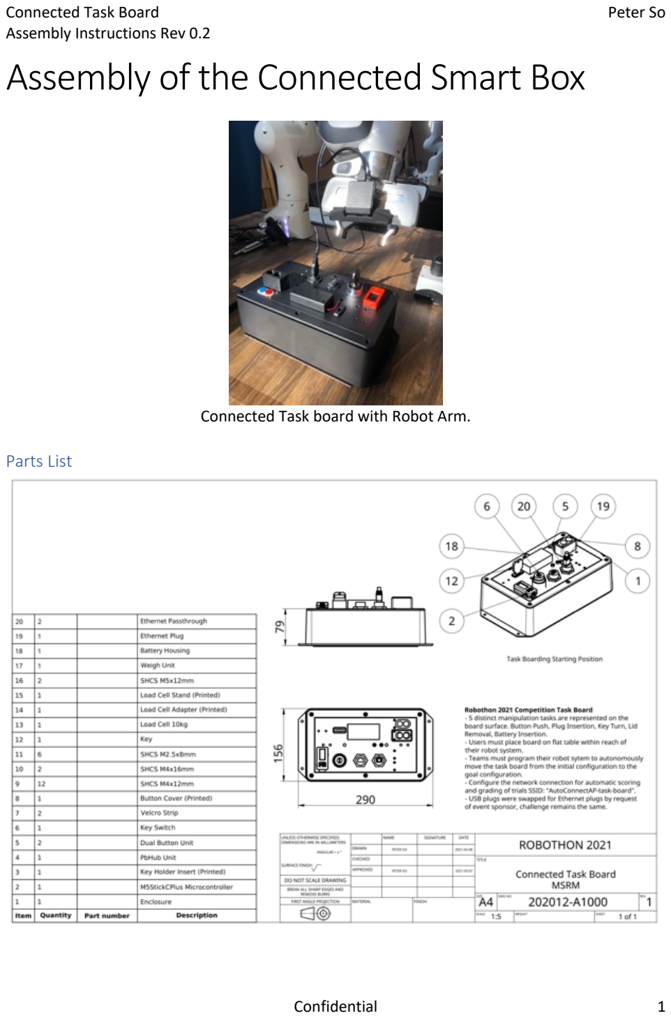
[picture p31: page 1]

Connected Task Board | Peter So
Assembly Instructions Rev 0.2
Confidential | 1

Connected Task board with Robot Arm.

Parts List

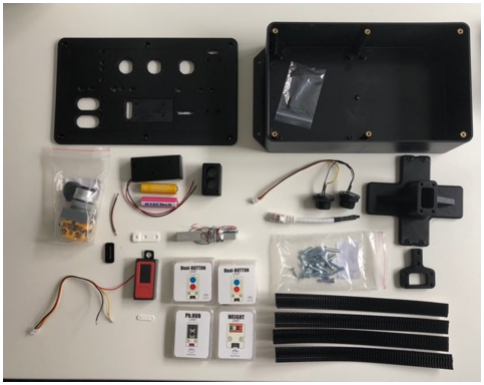
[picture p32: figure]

Parts laid out on table prior to assembly.

Procedure
1. Cut lid in CNC.
1.1. DXF File. CU-3286-MB parts - Cutout Template v3.dxf

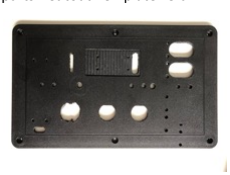
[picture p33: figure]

2. Print out parts in 3D Printer. Quantities are per task board.
2.1. LC Stand 1x,
2.2. Print out LC Mount 1x,
2.3. Key Holder 1x,
2.4. Button Cover 1x,
2.5. Lid Standoff 1x
3. Assemble the load cell column. Quantities are per task board.
3.1. Box-Stand (4x M3x8mm BHCS “Self-tapping” screw)
3.2. Load Cell Mount-Load Cell (2x M5x16mm SHCS)
3.3. Stand-Load Cell Mount (4x M4x16mm SHCS)

4. Mount components to lid.

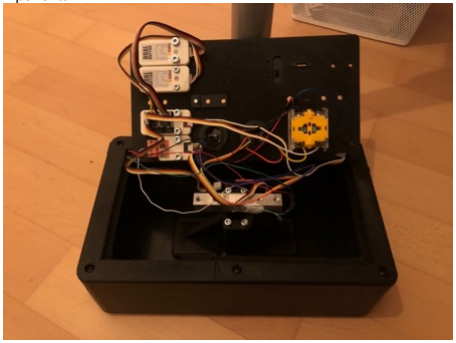
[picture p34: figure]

4.1. M5StickCPlus (2x M2x8mm SHCS)
4.2. Key Switch (Included with key switch). Key slot tip facing outward and cross the length of the task board.
4.3. RJ45 Port x2 (Included with port)
4.4. Dual Button Unit 2pcs (2x M4x12mm SHCS)
4.5. Weigh Unit (2x M4x12mm SHCS)
4.6. PbHub Unit (2x M4x12mm SHCS)
4.7. Battery Holder (2x M3x8mm FHCS). Slide open the lid and drill a countersink hole in the battery holder to match the pre-drilled holes in the box lid.
5. Wiring – Key Switch
5.1. Add wire jumper across terminals 12 and 24.
5.2. Trim off one connector of the grove cable and strip wires BLACK, YELLOW, WHITE.
5.3. Terminate grove cable on key switch. BLACK = 24, WHITE = 11, YELLOW = 23.
6. Wiring – Soldering for the RJ45 Ports

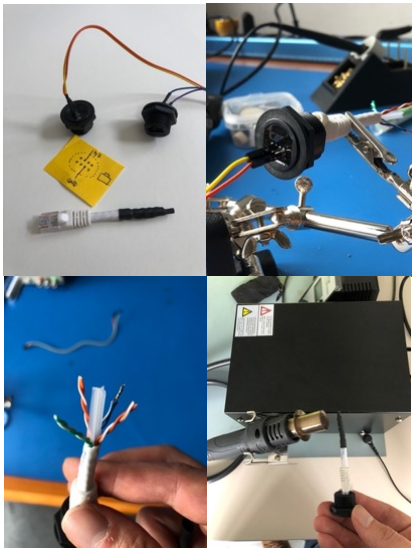
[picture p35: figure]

6.1. Terminate Grove Port Cables for the ethernet port Pins 2 and 7. See picture for pin identification and orientation.
6.2. Make Ethernet Dongle with shorted data wires BLUE and BLUE/WHITE and seal with heat shrink over solder joint and over entire cable.
7. Wiring – Connect Grove port cables to hub.
7.1. Hub Port Assignments
7.1.1. Port 0 – Dual Button Unit
7.1.2. Port 1 – Dual Button Unit (Covered)
7.1.3. Port 2 – Key switch
7.1.4. Port 3 – Ethernet Port
7.1.5. Port 4 – Empty (Reserved for Weigh Unit)
7.1.6. Port 5 – Empty
8. Upload Program to the M5StickC. <TODO provide final firmware>
8.1. Still need to figure out the
8.1.1. WiFi greeter feature
8.1.2. OTA software update feature

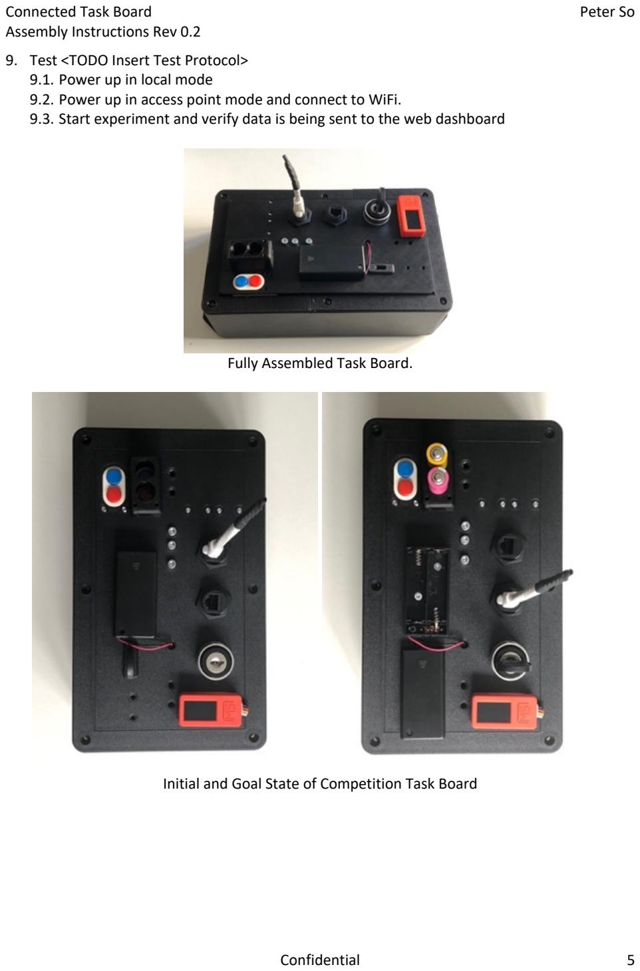
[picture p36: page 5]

9. Test <TODO Insert Test Protocol>
9.1. Power up in local mode
9.2. Power up in access point mode and connect to WiFi.
9.3. Start experiment and verify data is being sent to the web dashboard

Fully Assembled Task Board.

Initial and Goal State of Competition Task Board

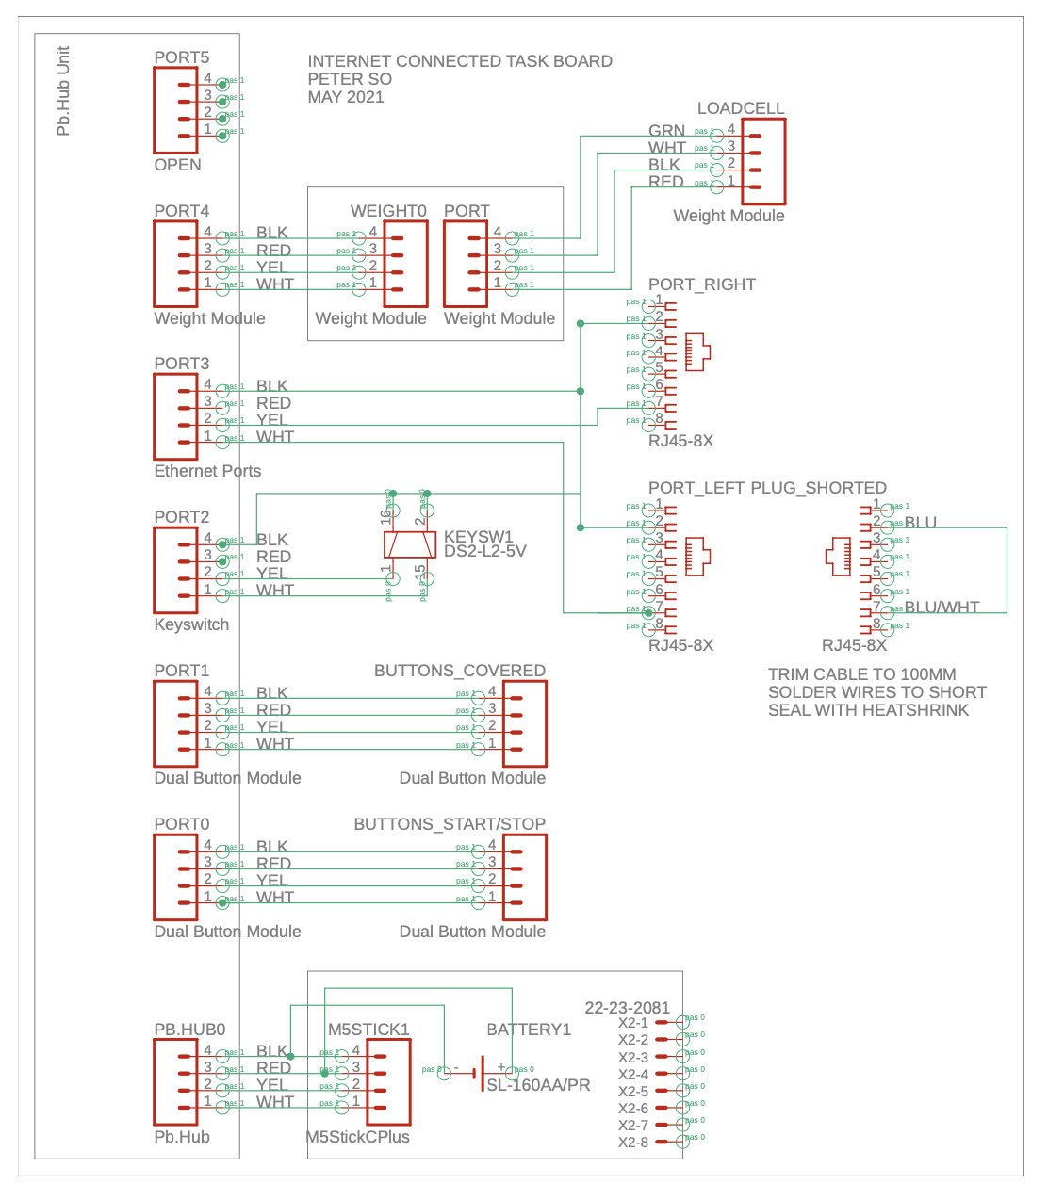
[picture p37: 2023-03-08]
assets/manufacturing/TBv2021-TBv2022/TaskBoardWiringV2.png

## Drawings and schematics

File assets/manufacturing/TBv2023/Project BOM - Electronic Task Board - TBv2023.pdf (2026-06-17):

Project BOM - IoT Fidget Cube / Task Board | Design BOM v2023

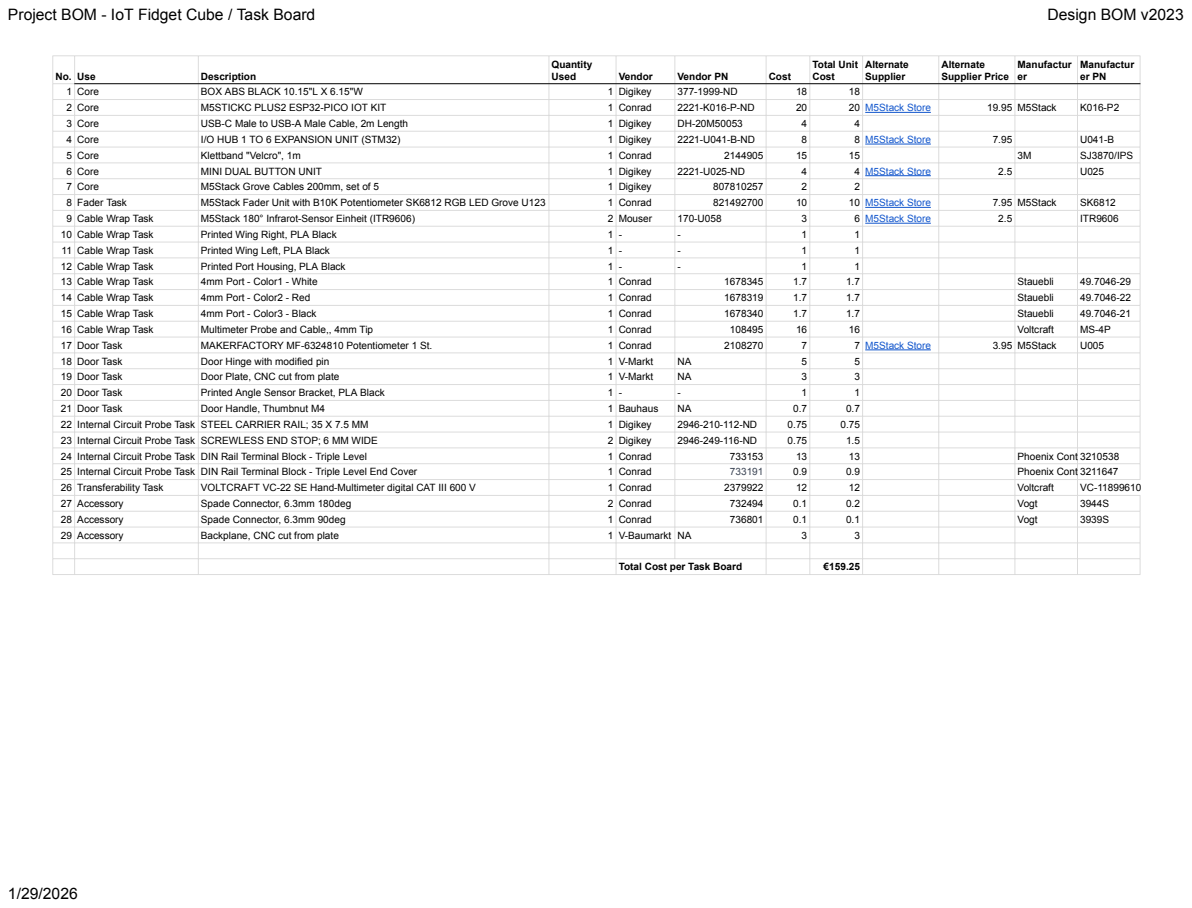
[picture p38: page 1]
No. Use; Description; Quantity; Used; Vendor; Vendor PN; Cost; Total Unit Cost; Alternate Supplier; Alternate Supplier Price; Manufactur er; Manufactur er PN; Total Cost per Task Board; 1 Core; BOX ABS BLACK 10.15"L X 6.15"W; 1 Digikey; 2 Core; M5STICKC PLUS2 ESP32-PICO IOT KIT; 1 Conrad; 19.95 M5Stack; 3 Core; USB-C Male to USB-A Male Cable, 2m Length; 4 Core; I/O HUB 1 TO 6 EXPANSION UNIT (STM32); 5 Core; Klettband "Velcro", 1m; SJ3870/IPS; 6 Core; MINI DUAL BUTTON UNIT; 7 Core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

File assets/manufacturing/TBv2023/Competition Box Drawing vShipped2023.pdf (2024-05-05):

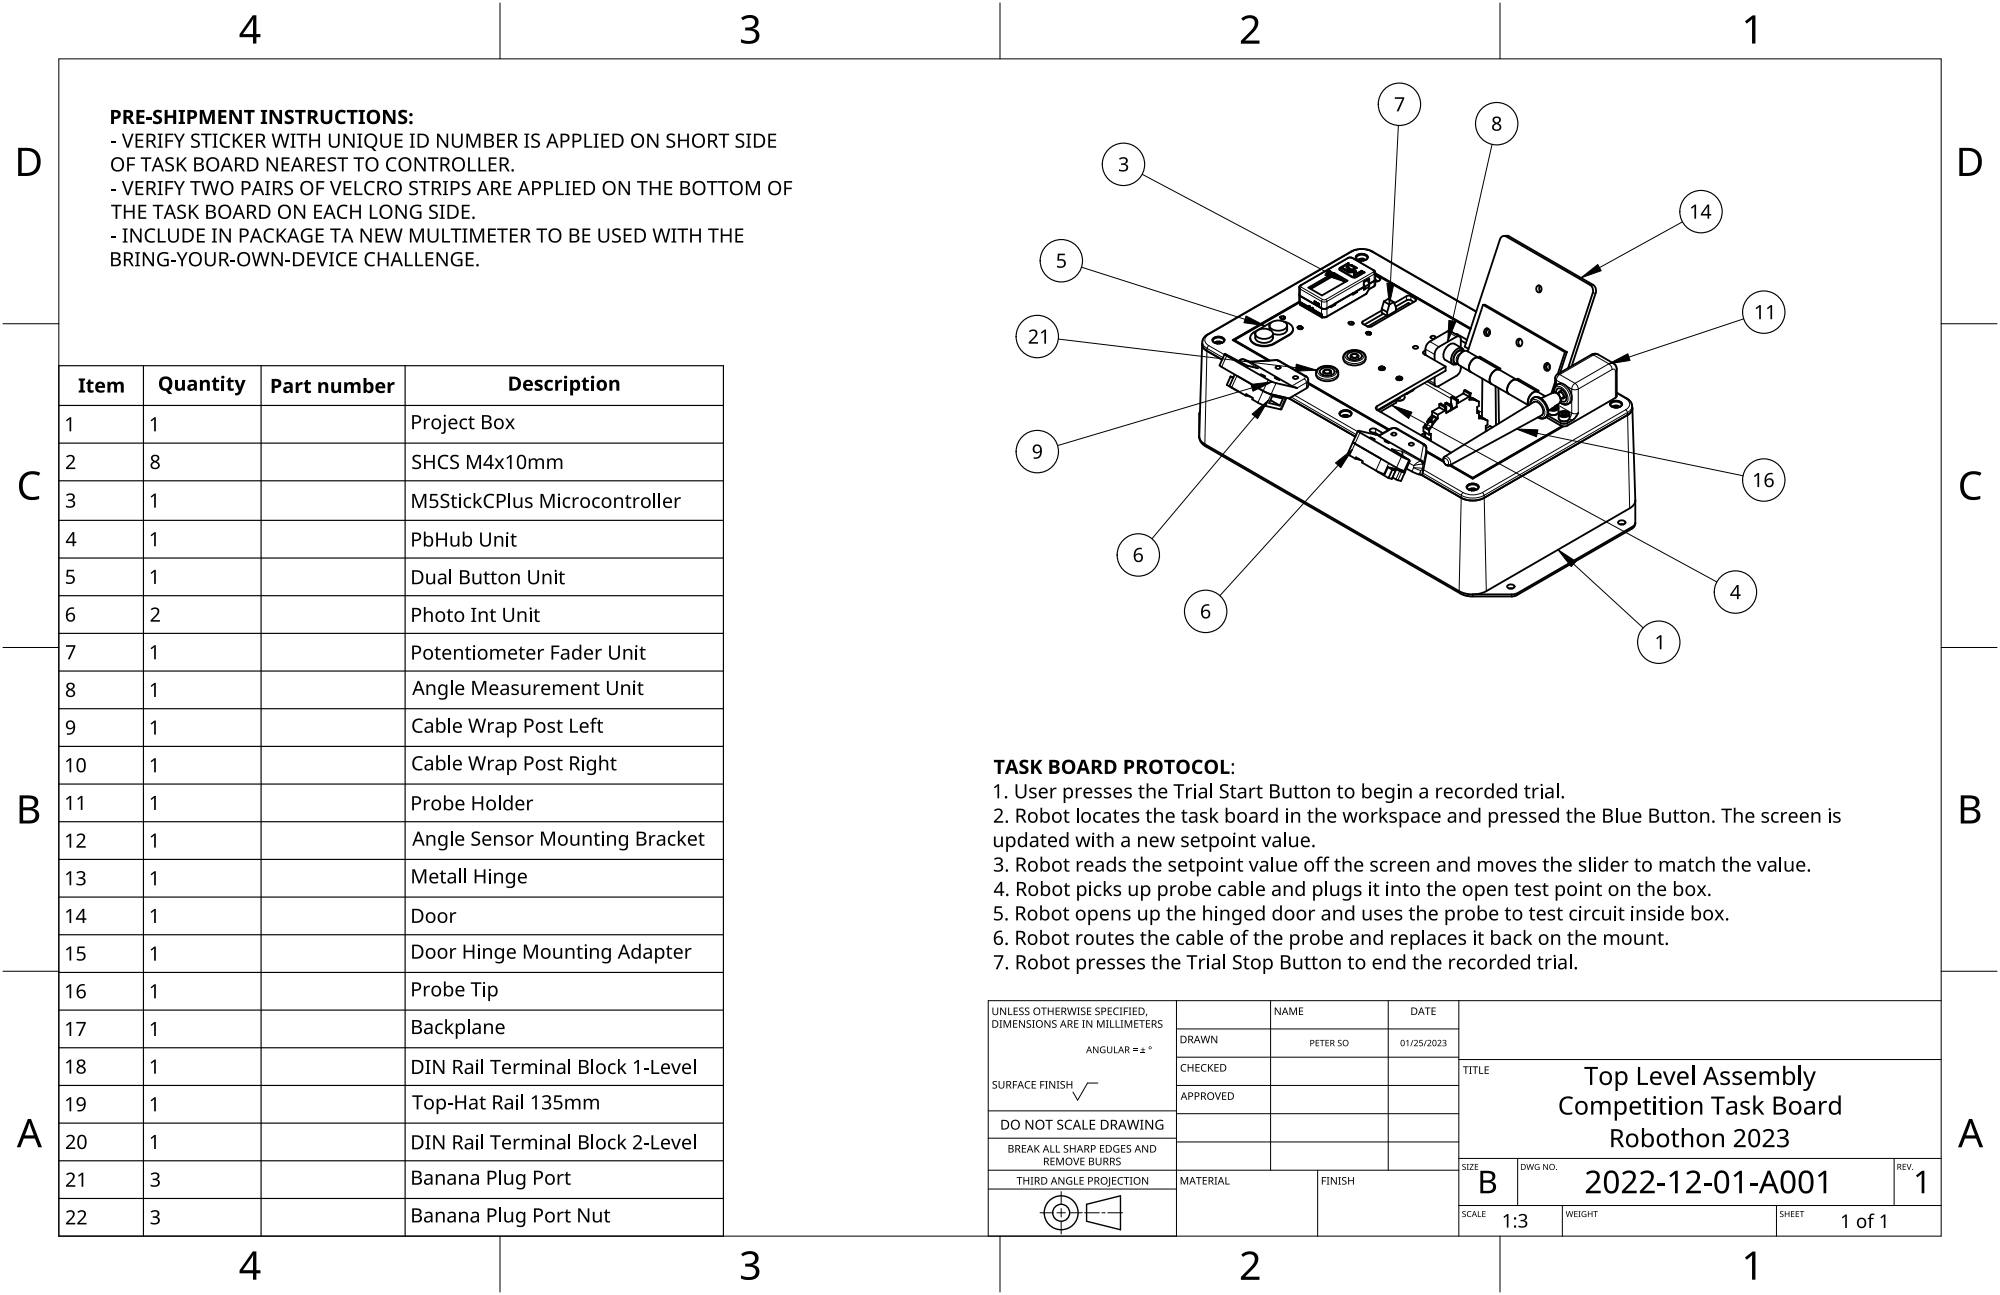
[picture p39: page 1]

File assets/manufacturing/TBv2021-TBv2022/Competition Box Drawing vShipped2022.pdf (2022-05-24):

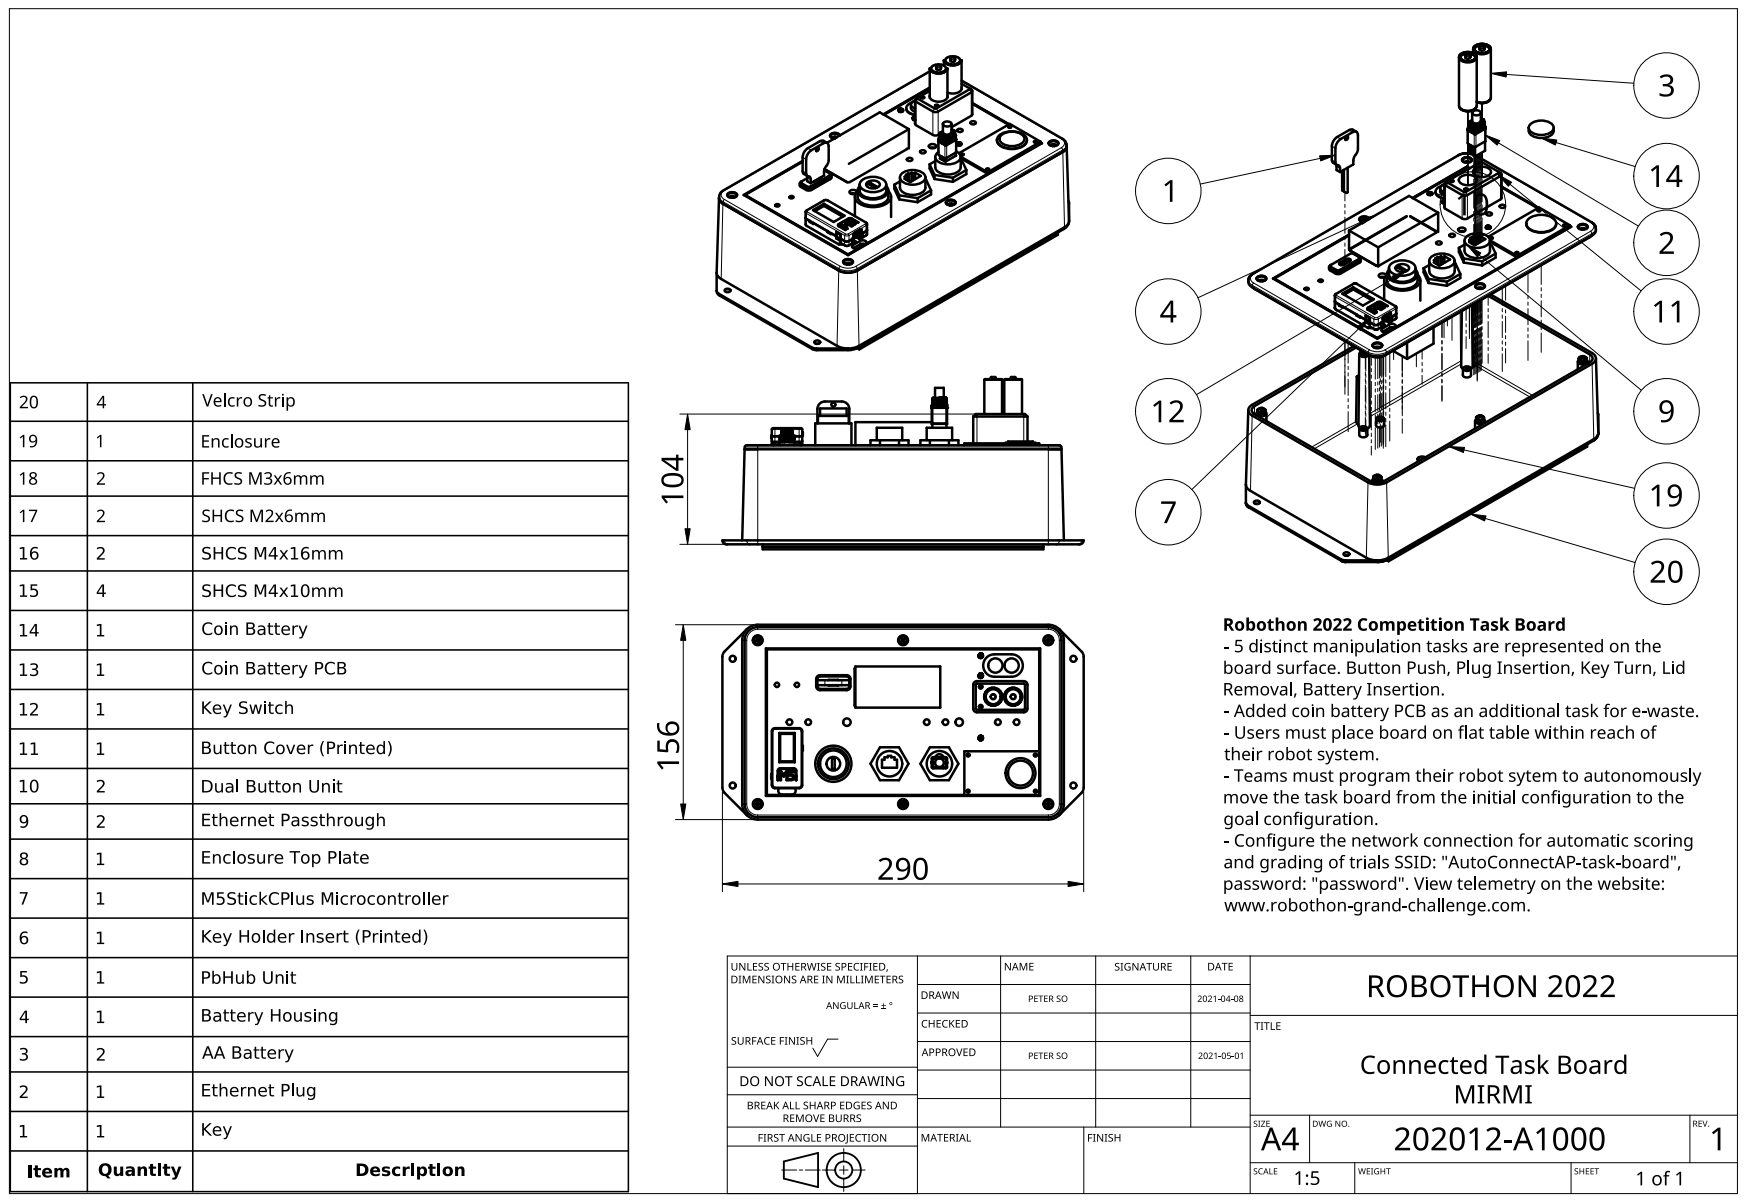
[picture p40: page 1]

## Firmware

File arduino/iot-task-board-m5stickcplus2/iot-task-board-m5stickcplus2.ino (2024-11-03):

// This is a program to measure manipulation performance with the Electronic Task Board.
// First written by Peter So, December 2020.
// Last updated July 2024
//
// Program will not run on board without being connected to the PbHub unit.
// Default behavior is board will attempt to WiFi network. Hold M5 button during power up to use without WiFi.
//
#include <M5StickCPlus2.h>  // https://github.com/m5stack/M5StickC-Plus
#include <Preferences.h>
#include <Wire.h>
#include "porthub.h"
#include <WiFiManager.h>  // https://github.com/tzapu/WiFiManager
#include <WiFi.h>
#include <WiFiClient.h>
#include <PubSubClient.h>
#include <ArduinoJson.h>
#include <HTTPClient.h>
#include <HTTPUpdate.h>

// USER CONFIGURABLE SETTINGS
#define TASK_BOARD_PW "robothon"
#define PROTOCOL_ID "ROBOTHON_2023"
#define TIMELIMIT 600      // Trial Time Limit in seconds (600 is 10min)
#define FADERSP 2000       // This value should be updateable via the web commands from Kaa
#define FADERSP2 1500      // This value should be updateable via the web commands from Kaa
#define FADERTOLERANCE 60  // This value should be updateable via the web commands from Kaa
#define ANGLESP 2400       // Make sure this works for all task boards with the installed set screw
#define PTS_BUTTON 1
#define PTS_FADER 1
#define PTS_CIRCUIT_PROBE 1
#define PTS_CABLEWRAP 1
#define PTS_PROBEINSERT 1

#define MAC WiFi.macAddress()
#define BUTTON_ON 0
#define BUTTON_OFF 1
#define SCREEN_ROWS 135  // pixels
#define SCREEN_COLS 240  // pixels

// This value should be updateable via the web commands from Kaa
int verbose = 0;  // set to 1 to enable serial output, default 0

//////// TASK BOARD SPECIFIC SETTINGS /////////
const String TOKEN = "task_board_dev";                // Endpoint token - you get (or specify) it during device provisioning
const String APP_VERSION = "c1v9jqmgul2l1s47m6bg-v0";  // Application version - you specify it during device provisioning
// const String APP_VERSION = "bvhkhrtbhnjc0btkj7r0-v0";    // Application version - you specify it during device provisioning FOR DEVELOPMENT ONLY
const String FW_VERSION = "1.1.1";  // Firmware Version for OTA management
//////// TASK BOARD SPECIFIC SETTINGS /////////

// DO NOT CHANGE SETTINGS BELOW //
const char* mqtt_server = "mqtt.cloud.kaaiot.com";

const unsigned long trialPublishRate = 1 * 1 * 1000UL;  //1000ms this should be something small like 5Hz or 200ms
const unsigned long fiveSeconds = 1 * 5 * 1000UL;       //5000ms or 5 seconds
static unsigned long lastPublish = 0 - fiveSeconds;

// Setup Persistent Memory
Preferences myPrefs;  //declare a namespace for the non-volatile memory (NVM)

// Setup PbHub device
PortHub porthub;
uint8_t HUB_ADDR[6] = { HUB1_ADDR, HUB2_ADDR, HUB3_ADDR, HUB4_ADDR, HUB5_ADDR, HUB6_ADDR };

// Setup WiFi and PubSub client
WiFiClient espClient;
PubSubClient client(espClient);

// Setup stopwatch interrupt specific settings
// timer interrupt variable.
volatile unsigned long usecCount = 0;

// hw_timer_t *interruptTimer = NULL;
// portMUX_TYPE mutex = portMUX_INITIALIZER_UNLOCKED;
// void IRAM_ATTR usecTimer()
// {
//   portENTER_CRITICAL_ISR(&mutex);
//   usecCount += 5;
//   portEXIT_CRITICAL_ISR(&mutex);
// }

///////////////////////////////
/////// INITIALIZE VARS ///////
///////////////////////////////

// Initialize program variables before running the setu and main loops
String task_board_ssid, unique_ssid;

//min,sec,msec,usec display.
int display[4] = { 0 };
unsigned long now = 0;
unsigned long last = 0;
unsigned long scan_time = -1;
unsigned long startTime = 0;

//timer start/stop check variable
int screenSelector = 0;  // int to navigate multiple screens
int screenSelector_count = 0;
int coin = 0;

int forceStop = 0;
int trialCounter = 0;
int humanAttempts = 0;
unsigned long trialTime = 0;
int wifiEnabled = 0;
int countStart = 0;
int trialRunning = 0, timeLeft = 0, ptsCollected = 0;
int buttonPushLatch = 0, faderLatch = 0, angleLatch = 0, angleDoorLatch = 0, cableWrapProbeStowLatch = 0, cableWrapLatch = 0, probeGoalLatch = 0, OP180_1_Latch = 0, OP180_2_Latch = 0, trialCompletedLatch = 0;
int faderLatch2 = 0;
int faderGoal2 = 0;
int humanStart = 0;

int startBtnState = -1, stopBtnState = -1, resetBtnState = -1, buttonPushState = -1, faderValue = -1;
int keyswitchRState = -1, keyswitchLState = -1, angleValue = -1, portRState = -1, portLState = -1;
int probeStartState = -1, probeGoalState = -1, OP180_1_State = -1, OP180_2_State = -1, buttonPushState_old = -1;
int stopBtnState_old = -1, faderValue_old = -1, angleValue_old = -1, probeStartState_old = -1, probeGoalState_old = -1;
int OP180_1_State_old = -1, OP180_2_State_old = -1;

int TS_button = 0, TS_fader_mid = 0, TS_fader = 0, TS_angle = 0, TS_angle_door = 0, TS_cableWrap = 0, TS_cableWrapProbeStow = 0, TS_probeGoal = 0, TS_OP180_1 = 0, TS_OP180_2 = 0, TS_finalTrialTime = 0;

float force = 0.0F, cumForce = 0.0F;
float startaccX = 0.0F, startaccY = 0.0F, startaccZ = 0.0F;
float load = 0.0F;
float accX = 0.0F, accY = 0.0F, accZ = 0.0F;
float gyroX = 0.0F, gyroY = 0.0F, gyroZ = 0.0F;
float pitch = 0.0F, roll = 0.0F, yaw = 0.0F;
float temp = 0.0F;

uint8_t BoardState[6] = { startBtnState, resetBtnState, faderValue, angleValue, probeStartState, probeGoalState };

/////////////////////////////////
// Custom Function Definitions //
/////////////////////////////////
void callback(char* topic, byte* payload, unsigned int length) {
  Serial.printf("\nHandling command message on topic: %s\n", topic);

  //Check if message is related to the OTA update
  if (String(topic).startsWith("kp1/" + APP_VERSION + "/cmx_ota/" + TOKEN)) {
    handleOtaUpdate(topic, payload, length);  //seems to be running with every message related to cmx_ota... remove this and only check for new firmawre on powerup.
    return;
  }

  //Check if message is related to a command message
  if (!String(topic).startsWith("kp1/" + APP_VERSION + "/cex/" + TOKEN)) {
    // TODO: Debug handling of command messages sent from the Kaa dashboard
    return;
  }

  DynamicJsonDocument doc(2048);
  deserializeJson(doc, payload, length);
  JsonVariant json_var = doc.as<JsonVariant>();

  DynamicJsonDocument commandResponse(2048);
  for (int i = 0; i < json_var.size(); i++) {
    unsigned int command_id = json_var[i]["id"].as<unsigned int>();
    commandResponse.createNestedObject();
    commandResponse[i]["id"] = command_id;
    commandResponse[i]["statusCode"] = 200;
    commandResponse[i]["payload"] = "done";
  }

  String responseTopic = "kp1/" + APP_VERSION + "/cex/" + TOKEN + "/result/SWITCH";
  client.publish(responseTopic.c_str(), commandResponse.as<String>().c_str());
  Serial.println("Published response to SWITCH command on topic: " + responseTopic);

  // Receive and parse the payload
  Serial.println("Payload: " + doc.as<String>());  //TODO troubleshoot
}

void setup_wifi() {
  if (WiFi.status() != WL_CONNECTED) {
    delay(200);
    Serial.println();
    Serial.printf("Connecting to [%s]", unique_ssid);
    WiFi.begin(unique_ssid.c_str(), TASK_BOARD_PW);
    connectWiFi();
  }
}

void connectWiFi() {
  while (WiFi.status() != WL_CONNECTED) {
    delay(500);
    Serial.print(".");
  }
  Serial.println();
  Serial.println("WiFi connected");
  Serial.println("IP address: ");
  Serial.println(WiFi.localIP());
}


void initServerConnection() {
  setup_wifi();
  if (!client.connected()) {
    reconnect();
  }
  client.loop();
}

void reconnect() {
  while (!client.connected()) {
    Serial.println("Attempting MQTT connection...");
    char* client_id = "client-id-123ab";
    if (client.connect(client_id)) {
      Serial.println("Connected to WiFi");
      // ... and resubscribe
      subscribeToCommand();
    } else {
      Serial.print("failed, rc=");
      Serial.print(client.state());
      Serial.println(" try again in 5 seconds");
      // Wait 5 seconds before retrying
      delay(5000);
    }
  }
}

void subscribeToCommand() {
  String topic = "kp1/" + APP_VERSION + "/cex/" + TOKEN + "/command/SWITCH/status";
  client.subscribe(topic.c_str());
  Serial.println("Subscribed on topic: " + topic);

  //Inserting from OTA Example function subscribeToFirmwareUpdates()
  String serverPushOnConnect = "kp1/" + APP_VERSION + "/cmx_ota/" + TOKEN + "/config/json/#";
  client.subscribe(serverPushOnConnect.c_str());
  Serial.println("Subscribed to server firmware push on topic: " + serverPushOnConnect);

  String serverFirmwareResponse = "kp1/" + APP_VERSION + "/cmx_ota/" + TOKEN + "/config/json/status/#";
  client.subscribe(serverFirmwareResponse.c_str());
  Serial.println("Subscribed to server firmware response on topic: " + serverFirmwareResponse);

  String serverFirmwareErrorResponse = "kp1/" + APP_VERSION + "/cmx_ota/" + TOKEN + "/config/json/status/error";
  client.subscribe(serverFirmwareErrorResponse.c_str());
  Serial.println("Subscribed to server firmware response on topic: " + serverFirmwareErrorResponse);
}

//OTA Functions from Kaa
void reportCurrentFirmwareVersion() {
  String reportTopic = "kp1/" + APP_VERSION + "/cmx_ota/" + TOKEN + "/applied/json";
  String reportPayload = "{\"configId\":\"" + FW_VERSION + "\"}";  //UPDATE this to match the OTA upgradeable from field on Kaa
  Serial.println("Reporting current firmware version on topic: " + reportTopic + " and payload: " + reportPayload);
  client.publish(reportTopic.c_str(), reportPayload.c_str());
}

void requestNewFirmware() {
  int requestID = random(0, 99);
  String firmwareRequestTopic = "kp1/" + APP_VERSION + "/cmx_ota/" + TOKEN + "/config/json/" + requestID;
  Serial.println("Requesting firmware using topic: " + firmwareRequestTopic);
  client.publish(firmwareRequestTopic.c_str(), "{\"observe\":true}");  // observe is used to specify whether the client wants to accept server pushes
}

void handleOtaUpdate(char* topic, byte* payload, unsigned int length) {
  Serial.printf("\nHandling firmware update message on topic: %s and payload: ", topic);

  //DEBUG with Denys
  //This fixed the issue!
  //This checks that the topic is indeed a cmx_ota message.
  if (!String(topic).startsWith("kp1/" + APP_VERSION + "/cmx_ota/" + TOKEN)) {
    return;
  }
  //END DEBUG

  DynamicJsonDocument doc(1023);
  deserializeJson(doc, payload, length);
  JsonVariant json_var = doc.as<JsonVariant>();
  Serial.println(json_var.as<String>());
  if (json_var.isNull()) {
    Serial.println("No new firmware version is available");
    return;
  }

  unsigned int statusCode = json_var["statusCode"].as<unsigned int>();
  if (statusCode != 200) {
    Serial.printf("Firmware message's status code is not 200, but: %d\n", statusCode);
    return;
  }

  //  return; //DEBUG escape do not actually update the firmware //commenting this line will enable OTA update.
  String firmwareLink = json_var["config"]["link"].as<String>();

  t_httpUpdate_return ret = httpUpdate.update(espClient, firmwareLink.c_str());

  switch (ret) {
    case HTTP_UPDATE_FAILED:
      Serial.printf("HTTP_UPDATE_FAILED Error (%d): %s\n", httpUpdate.getLastError(), httpUpdate.getLastErrorString().c_str());
      break;

    case HTTP_UPDATE_NO_UPDATES:
      Serial.println("HTTP_UPDATE_NO_UPDATES");
      break;

    case HTTP_UPDATE_OK:
      Serial.println("HTTP_UPDATE_OK");
      break;
  }
}

void resetCounter() {
  myPrefs.begin("task-board", false);
  myPrefs.clear();  //remove all key-value pairs in namespace
  myPrefs.end();
  myPrefs.remove("trialCounter");  // Or remove the counter key only.
  trialCounter = myPrefs.getUInt("trialCounter", 0);  // Get the counter value in current namesapce, if no key exists then return default value as second parameter
  myPrefs.remove("humanAttempts");  // Or remove the counter key only.
  humanAttempts = myPrefs.getUInt("humanAttempts", 0);  // Get the counter value in current namesapce, if no key exists then return default value as second parameter
  Serial.printf("Trial Counter value reset!\n");  // Print the counter to Serial Monitor.
}
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

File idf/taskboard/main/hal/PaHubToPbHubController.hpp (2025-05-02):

/**
 * Robothon Task Board Firmware
 */

#pragma once

#include <M5Unified.h>

#include <hal/PbHubController.hpp>

#include <esp_log.h>

#include <cstdint>

/**
 * @struct PaHubController
 * 
 * @brief Controller for I2C communication with PaHub device
 * 
 */
struct PaHubController
{
    const char* TAG = "PaHubController";    ///< Logging tag

    static constexpr uint32_t I2C_FREQ = 400000;        ///< I2C bus frequency in Hz
    static constexpr uint8_t PAHUB_I2C_ADDR = 0x70;   ///< Default I2C address for PaHub

    /**
     * @brief Constructs a new PaHubController object
     *
     * @details Initializes I2C communication with default address
     */
    PaHubController() noexcept
        : i2c_addr_(PAHUB_I2C_ADDR)
    {
        bool init = M5.Ex_I2C.begin();

        if (init)
        {
            ESP_LOGI(TAG, "PaHubController::PaHubController() on address %d", i2c_addr_);
        }
        else
        {
            ESP_LOGE(TAG, "PaHubController::PaHubController() failed");
        }
    }

    /**
     * @brief Selects the TCA9548A I2C multiplexer channel
     *
     * @param bus Target bus number
     *
     * @return true if operation successful, false otherwise
     */
    bool TCA9548A_select(uint8_t bus)
    {
        bool status = true;

        if (bus != last_channel_selected_)
        {
            status = status && M5.Ex_I2C.start(i2c_addr_, false, I2C_FREQ);
            status = status && M5.Ex_I2C.write(1 << bus);
            status = status && M5.Ex_I2C.stop();
            if (status)
            {
                last_channel_selected_ = bus;
                ESP_LOGI(TAG, "TCA9548A_select() bus %d selected", bus);
            }
        }

        return status;
    }

private:

    const uint8_t i2c_addr_ = 0;   ///< I2C address of PaHub device
    uint8_t last_channel_selected_ = -1;   ///< Last selected channel

};



/**
 * @struct PaHubToPbHubController
 *
 * @brief Controller for I2C communication with PbHub device through PaHub
 *
 */
struct PaHubToPbHubController :
    public PbHubController
{
    const char* TAG = "PaHubToPbHubController";    ///< Logging tag

    static constexpr uint8_t PBHUB_I2C_ADDR = 0x61;   ///< Default I2C address for PbHub

    /**
     * @brief Constructs a new PaHubToPbHubController object
     *
     * @details Initializes I2C communication with default address
     */
    PaHubToPbHubController(PaHubController& pa_hub_controller,uint8_t pb_hub_channel) noexcept
        :   i2c_addr_(PBHUB_I2C_ADDR),
            pa_hub_controller_(pa_hub_controller),
            pb_hub_channel_(pb_hub_channel)
    {
        bool init = M5.Ex_I2C.begin();

        if (init)
        {
            ESP_LOGI(TAG, "PaHubToPbHubController::PaHubToPbHubController() on address %d", i2c_addr_);
        }
        else
        {
            ESP_LOGE(TAG, "PaHubToPbHubController::PaHubToPbHubController() failed");
        }
    }
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

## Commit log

2021-02-08 add working demo of keyswitch with arduino IDE
2021-02-28 add linux arduino ide setup guide
2021-03-22 fix bug with batt2 and m5.begin with operation with battery
2021-03-23 added optional boot mode to connect to wifi (hold down M5 on power up
2021-03-25 add new device configuration still WIP
2021-04-16 updated wifi enable block to print on screen
2021-06-09 printer-files
    3d printing files for competition boards
2021-07-28 update the arduino readme and gitignore
2021-07-28 cleaned up device firmware
2021-07-28 added task board status updates to usb-serial, added gyro readings to publisher
2021-08-04 found a minimal working version to send esp32 telemetry to iotc
2021-08-04 beginning of an combined task board code WIP
2021-08-04 updated message fields to display on IOTC, also had to update the device template on IOTC to match, working
2021-12-02 added small readme for azure verification and required fixes for device.ino on m5stickcplus
2022-02-16 Adding task board status to print to serial
2022-02-17 cleaned up M5Stick LED Display, added serial output by default
2022-02-19 working OTA with task board code
2022-04-25 update task board state with left and right and kaa reporting
2022-05-24 update readmes and add CNC job file for cutting lids
    [Board Part Studio - ButtonCoverPlate m3.stl, CU-3286-MB parts - 3286-CT - Frame Single.stl, CU-3286-MB parts - 3286-CT - j2.stl, CU-3286-MB parts - 3286-CT -tr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]
2022-05-25 adding instructions for flashing firmware by end user without Arduino IDE
2023-02-13 cardboard prototype of 2023 task board FW and added wiring diagram
2023-02-28 add a dual publish rate for active trials at 20Hz when active
2023-03-04 added a bug fix for the STM32 PbHub units that have a floating value issue
2023-03-04 updated debug for new STM32 version
2023-03-04 improved screen flow: button to fader task, added post IO on ST5 cable wrap screen
2023-03-04 made ssid unique with component of device label
2023-03-08 adding CNC files
    [CU-3286-MB - Sketch MillingExportV3.dxf, Door - Task Board 2023.dxf]
2023-05-15 add task board v2023 and update readme
2024-07-29 working version of as-built task boards with new StickCP2 controller, fixed trial timer reset bug, trial progress bubbles bug with push button
2024-07-29 add batt voltage to screen and telemetry, fix slider task completion before button task bug, confirm angle sensor works, add timestamps to usb serial output
2024-07-29 add ST times to home screen, add timestamps for intermediate tasks slider SP1, opening door, wrapping cable around posts
2024-07-31 bug fix for timer reset and trial abort, add wrapped cable pre-start check, add batt info to screen and telemetry, add ST_times to screen
2024-07-31 improved the names of the telemetry fields for all task board events, backwards compatible with older task boards
2024-07-31 cleaned up the pre-start screen error messages, added a human start flag to filter data in post
2024-07-31 fix screen batt voltage bug
2024-08-05 intermediate version, found wifimanager bug with the pinMode set conflict, must use pin 19, not pin 10
2024-08-05 intermediate version working with new pin 19 and sending telemetry to kaa
2024-08-06 fixed NVM counter storage for persistent values over power cycles, fixed batt level on screen
2024-08-06 add method to reset NVM by pressing BtnB during powerup
2024-08-06 add method to reset NVM by pressing BtnB during powerup moved up before wifi manager
2024-08-07 fix slow clock by removing interrupt timer and replaced with millis()
2024-08-29 add method to manually reset stored wifi settings on device (pwr up while holding red and blue btns)
2024-10-29 update construction files for TBv2023 and links to euROBIN MSVC IROS 2024 competition
    [Angle Sensor Mounting Bracket - Angle Sensor Mounting Bracket.stl, Angle Sensor-Hinge Adapter.stl, Cable_Winding - Cable Wrap Post Left.stl, Cable_Winding - Ca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]
2024-11-13 Initial architecture
    [partitions.csv]
2024-11-21 Add SensorMeasurement Integer Type
2024-11-21 Add SensorCounter
2024-11-21 Task Step reset sensor status
2024-11-28 OTA Updates
    [partitions.csv]
2025-01-24 increased hole sizes for better assembly
    [CU-3286-MB - Box Lid V3-updated.dxf]
2025-01-24 reorganize manufacturing files
    [Angle Sensor Mounting Bracket - Angle Sensor Mounting Bracket.stl, Angle Sensor-Hinge Adapter.stl, Board Part Studio - ButtonCoverPlate m3.stl, CU-3286-MB - Bo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]
2025-03-04 Partitions file for StickC Plus.
    [partitions_stickcplus.csv]
2025-03-21 Blink LED on task completion
2025-04-09 Add touch screen sensor
2025-04-10 Generalize for any screen size. Filter points on path creation.
2025-04-16 Update default to Core2 device in menuconfig
2025-04-23 Actuator.hpp, TaskStepActuator.hpp Add actuators (LEDS and solenoid) and 2025 task steps to TaskBoardDriver_TBv2025.hpp
2025-04-23 Ball-drop solenoid actual hardware pin.
2025-05-03 update sensor and actuator pin assignments to match as-built
2025-05-03 update LED pin assignments and default task sequence to match desired test protocool
2025-05-03 change behavior of Core2BtnC to toggle on/off the solenoid for 500ms timer to avoid burning device
2025-05-06 fixed LED full on command
2026-03-19 add cable plugged check after probe goal step in protocol
2026-06-17 updated TBv2023 BOM and add 3d print file
    [TBv2023_PrintCompleteSet.3mf, TBv2023_PrintCompleteSet.gcode.3mf]
